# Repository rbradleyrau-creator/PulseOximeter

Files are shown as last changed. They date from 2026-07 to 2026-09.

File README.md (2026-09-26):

# Personal Pulse Oximeter

This repository contains the schematics, designs, and other information regarding the design of a personal Pulse Oximeter. As part of the design process, the overal pulse oximeter design was broken up into three smaller milestones to allow for easier testing and prototyping before moving on to a final design. More information on each of these milestones and the final design can be found via the links below.

## Milestone 1: SpO2 & HR Sensor 

  This milestone involves creating a breakout board that isolates the sensor to be used in the final system. The implementation includes an Optical Pulse Oximeter/Heart-Rate Sensor and a linear voltage regular connected to headers. Through this, an external processor can be programmed to interface with the sensor and testing can be performed to determine the best layout in the final design. This board will also be used to write firmware for the final design. 

  [Read More](https://github.com/rbradleyrau-creator/PulseOximeter/tree/main/Milestone_1%3ASpO2_%26_HR_Sensor)
  
## Milestone 2: STM32UO73KC Development Board 

  In this milestone, the pins of an STM32UO73KCU6 is connected to various headers for use in testing. In addition to the processor, the PCB also includes USB 2.0, 3.3V Buck Converter, and optional Battery power/charging. The goal of this milestone is to begin writing programs to the STM32 via USB/SWD for use in the final design and to determine the efficiency in of various batteries in powering the system.

  [Read More](https://github.com/rbradleyrau-creator/PulseOximeter/tree/main/Milestone_2%3ASTM32U073KC_Development_Board)

## Milestone 3: Display

  The main goal of this milestone is to write firmware for the STM32 that displays information to an IPS LCD Display. To begin writing this firmware, a 13P FFC breakout board was developed to allow the previously designed development board to interface with the chosen display.

  [Read More](https://github.com/rbradleyrau-creator/PulseOximeter/tree/main/Milestone_3%3ALCD_Display)

# Final Design [WIP]

  The final design for this project includes an SpO2/HR sensor connected to an STM32. The STM32 reads data from the sensor and displays it to the LCD display. The system incorporates a battery for portable use with a USB port for charging. The system also enters deep sleep when not in use which is controlled via an ON/OFF switch. The display features both the heartrate readings, SpO2 readings, and the remaining battery life. All the previously mentioned parts are combined into a single, double-sided PCB and encased inside a 3D printed enclosure. This enclosure includes padding just below the sensor along with an adjustable band allowing the device to be mounted to a finger.

  [Read More](https://github.com/rbradleyrau-creator/PulseOximeter/tree/main/Final_Design)

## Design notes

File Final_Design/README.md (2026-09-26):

# Final Design
<div align="center">
  <div style="overflow-x: auto; gap: 10px; padding-bottom: 10px; white-space: nowrap; display: inline-block; margin-right: 10px;">
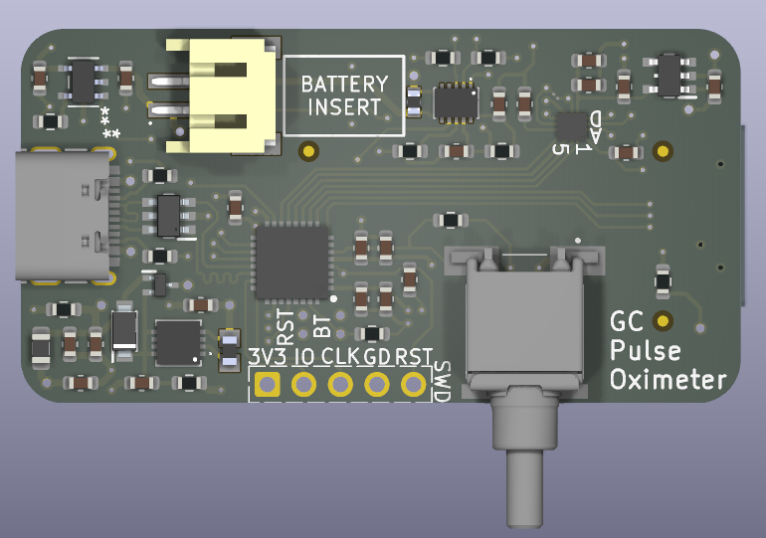
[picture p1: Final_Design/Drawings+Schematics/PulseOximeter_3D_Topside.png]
    
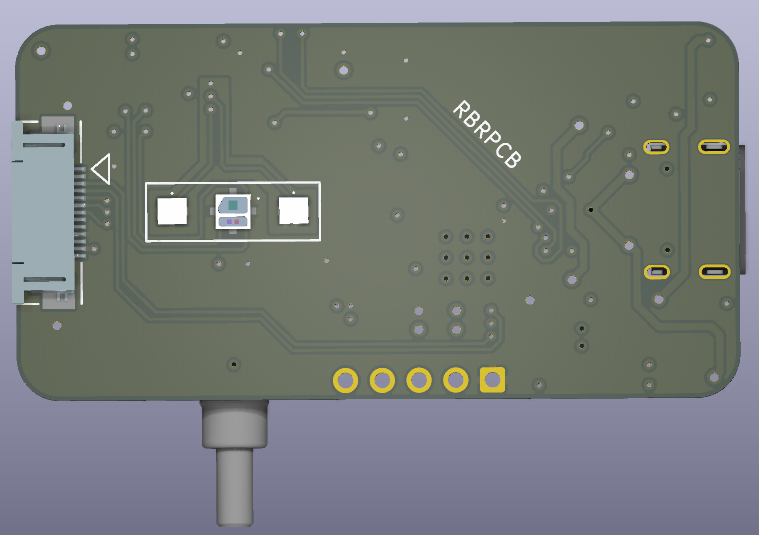
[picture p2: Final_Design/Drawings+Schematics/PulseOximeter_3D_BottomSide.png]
    
  </div>
  <br>
  
  <details>
    <summary><b>Click here to expand Copper Layers</b></summary>
    <br>
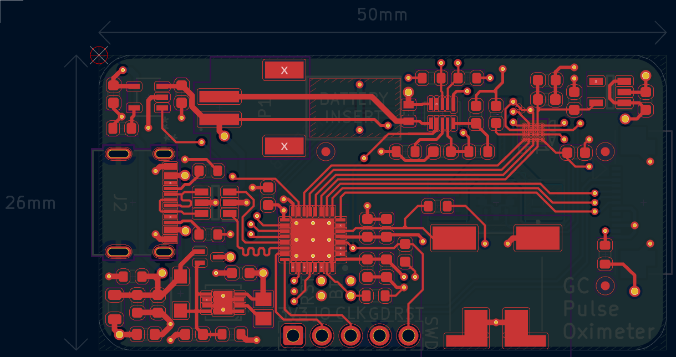
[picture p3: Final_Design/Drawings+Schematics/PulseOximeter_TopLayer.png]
    
    <hr>
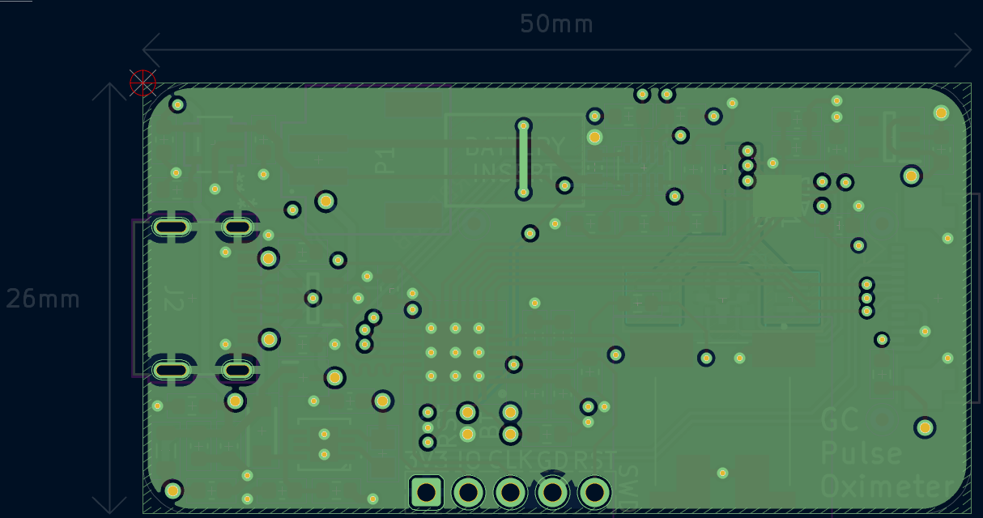
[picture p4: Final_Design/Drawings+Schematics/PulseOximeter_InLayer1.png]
SInner Layer 1
    
    <hr>
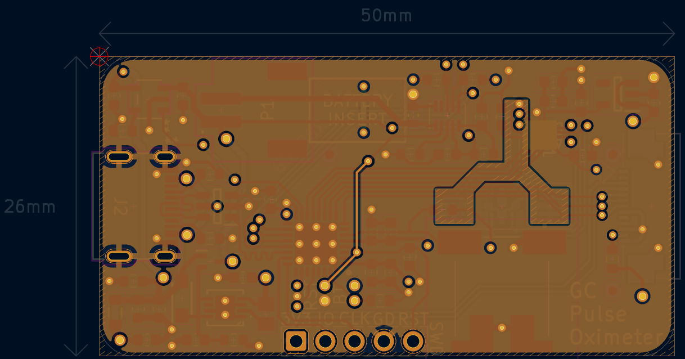
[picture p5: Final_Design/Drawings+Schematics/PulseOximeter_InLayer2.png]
Inner Layer 2
    
    <hr>
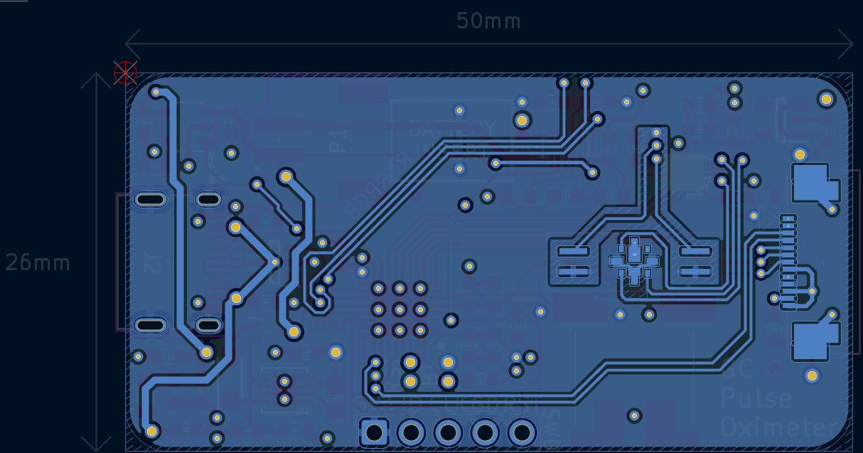
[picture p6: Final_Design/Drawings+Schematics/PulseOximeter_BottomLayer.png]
Bottom Layer
    
  </details>
</div>

<br>

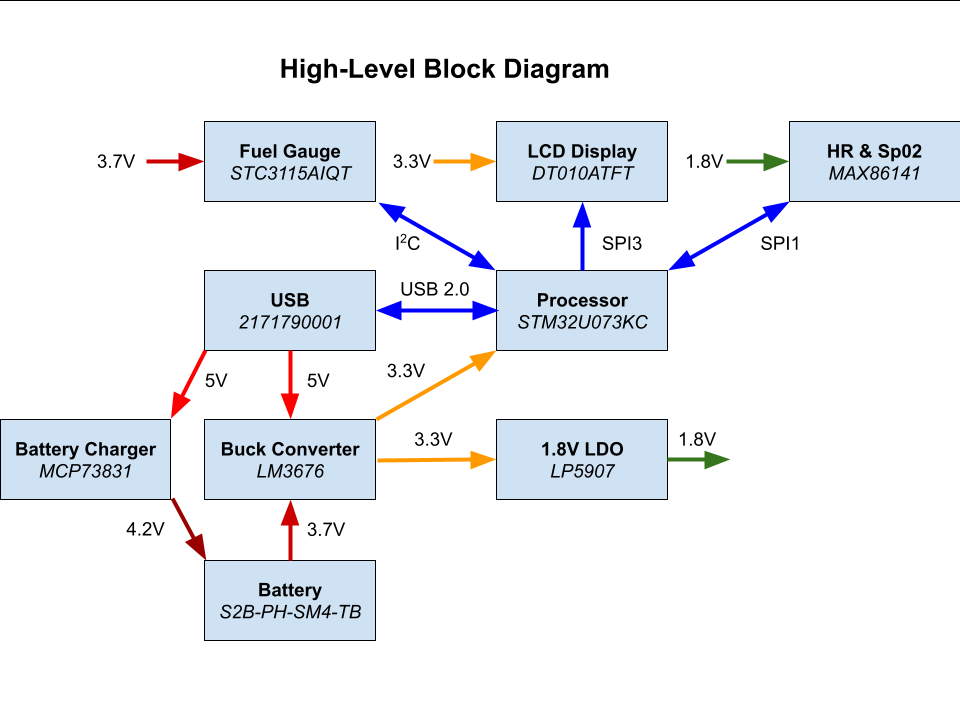
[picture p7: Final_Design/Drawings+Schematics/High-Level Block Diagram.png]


### Project Overview & Features
The final design consists of two major parts:
  - A PCBA containing each critical component
  - A 3D Modeled Enclosure to house the PCBA 

The PCB for the pulse oximeter combines all of the previous features into a singular board, with the STC3115AIQT as an exception. The board consists of an STM32U073KC processor connected to three peripherals: the STC3115AIQT fuel gauge over I2C, the MAX86141 HR/Sp02 sensor over SPI1, and an FFC connector over SPI3 for interfacing with the DT010ATFT LCD display. In addition, the processor is also connected to USB 2.0 and has SWD, boot, and reset access via exposed plated through holes. 

<br clear="right"/>
  Aside from those connections, the board operates on 3.3Vwhich is provided by the LM3676 buck converter. This component is supplied with anywhere from 5.5V (USB) to 3.0V (Battery), all of which are valid voltages for the LM3676 and a large factor for why the part was chosen. The board also includes MCP73831T battery charger which charges the battery whilst the USB is connected. 
  <br><br>
  The enclosure that houses this PCB measures at 3cm wide, 6cm long, and approximately 2cm tall and is designed for 3D printing. It is separated into two pieces that contain four dowels for a secure connection, however, the strength of this connection varies from printer to printer. In addition, the enclosure provides four openings in its casing: one at the bottom for the LED and photodiodes of the sensor, one at the top for the LCD Display, one on the side for the ON/OFF button, and one in the rear for USB port access. 

### Design Process

  The main schematic design of the PCB is largely a combination of the previous three boards into one singular board, however with some exceptions. Firstly, the TPB4056B battery charger was replaced with the MCP73831T. This was due to the fact that the TPB took up significant area on the PCB and was no longer available at the selected PCB manufacturer. A second change was the inclusion of the STC3115AIQT fuel gauge. This part was included in order to better gauge the battery life of the attached 3.7V Li-ion battery, since the discharge curve of Li-ion batteries are largely non-linear. One final design decision was the inclusion of plated through-holes for debugging. The decision was made in order to debug the newly included component and to avoid additional costs incurred due to additional manufacturing. 
  <br><br>
	For layout, the design was based around a centralized STM32 with the external connectors (USB, PH connector, ON/OFF switch, etc) being positioned in a way that made sense with the intended device enclosure. The board stack up was 4 layers with the top and bottom layers acting as signal layers and the internal layers as ground planes (with a few exceptions). One major design challenge that came up in the making of this board was the 3.3V plane that existed on the bottom of the board. Due to the large number of interconnections, this plane was broken up in several areas leading to vias being omitted from the plane or being connected by thin copper polygons. To fix this issue, components were moved to areas where they could source higher current in addition to a bridge through layer 2 to connect two un-connected polygons in the plane.
  <br><br>
	A second challenge in the design came from the placement of the LM3676 buck converter in relation to the USB data lines. Due to the required placement of the PH connector, the buck converter was located in the bottom left corner. To prevent the high-frequency switching from affecting sensitive components,  sensitive ICs like the MAX86141 IC were placed in the opposite corner of the board. However, the data lines of the USB could not be relocated. To minimize the effect this switching would have on these lines, the STM32 was shifted upward to allow the maximum distance between the data lines and the offending trace. This distance ended up being 5 times larger than the trace width of the data lines, providing satisfactory protection for full-speed USB.
  <br><br>
	A third challenge that came up in the design was the routing of SPI. Originally, the board was designed to operate with only one MOSI & MISO. However, this would have required a star connection scheme, resulting in disconnected ends causing reflections and ringing. To remove this factor, tertiary SPI pins on the STM32 were used to set up two separate communications. While this did take up more real estate on the board, it did allow for the display and MAX86141 connections to operate at different clocking frequencies which allowed the refresh rate of the DT010ATFT to quadruple. 

### Testing and Results

 As of 9/26/2026, the board is still in manufacturing and will be programmed and validated upon arrival. 

## List of Major Components/Datasheets

Sensors/Processors <br>
 - [STM32U073KCU6](https://www.st.com/resource/en/datasheet/stm32u073c8.pdf) <br>
 - [HR/Sp02 Sensor - MAX86141](https://www.analog.com/media/en/technical-documentation/data-sheets/max86140-max86141.pdf) <br>
 - [Fuel Gauge -STC3115AIQT](https://www.st.com/content/ccc/resource/technical/document/datasheet/24/05/c6/c7/0c/72/41/39/DM00066800.pdf/files/DM00066800.pdf/jcr:content/translations/en.DM00066800.pdf) <br>

Power 
- [Buck Converter - LM3676](https://www.ti.com/lit/ds/symlink/lm3676.pdf?ts=1784331233319&ref_url=https%253A%252F%252Fwww.ti.com%252Fproduct%252FLM3676) <br>
- [Battery Charger IC - MCP73831](https://www.mouser.com/datasheet/3/282/1/MCP73831_Family_Data_Sheet_DS20001984H.pdf) <br>
- [LDO - LP5907](https://www.ti.com/lit/ds/symlink/lp5907.pdf) <br>

Diodes/MOSFETs
- [Schottky Diode - NSR0620P2](https://www.onsemi.com/pdf/datasheet/nsr0620p2-d.pdf) <br>
- [P-Channel MOSFET - DMG1013T](https://www.diodes.com/datasheet/download/DMG1013T.pdf) <br>
- [ESD Diodes - USBLC6-2SC6Y](https://www.st.com/resource/en/datasheet/usblc6-2sc6y.pdf) <br>
- [LED(s) - SFH 7018B](https://www.mouser.com/datasheet/3/5912/1/SFH_7018B_EN.pdf) <br>
- [Photodiode - SFH 2704](https://www.mouser.com/datasheet/3/5912/1/SFH_2704_EN.pdf) <br>

Connectors
- [USB Connector - 2171790001](https://www.molex.com/en-us/products/part-detail/2171790001?display=pdf&utm_source=M2X&utm_medium=api&utm_campaign=api&utm_id=M2X_API?utm_source=M2X&utm_medium=api&utm_campaign=api&utm_id=M2X_API) <br>
- [13P FFC Connector - 527451397](https://www.molex.com/en-us/products/part-detail-pdf/527451397?display=pdf) <br>
- [Battery Connector - S2B-PH-SM4-TB](https://www.jst-mfg.com/product/pdf/eng/ePH.pdf) <br>
- [ON/OFF Switch - EP11SD1SAPE](https://www.littelfuse.com/assetdocs/littelfuse-ck-pushbutton-ep-series-datasheet?assetguid=1bab3baa-d70e-403b-9074-f0060fd8bd56)<br>

Peripherals
- [LCD Display - DT010ATFT](https://www.mouser.com/datasheet/3/3687/1/DT010ATFT-Rev1_1-Displaytech-Spec.pdf) <br>
- [Battery - 3.7V Li-ion](https://cdn-shop.adafruit.com/product-files/1570/1570datasheet.pdf) <br>

***

### [Return to Project Page](https://github.com/rbradleyrau-creator/PulseOximeter/tree/main) <br>

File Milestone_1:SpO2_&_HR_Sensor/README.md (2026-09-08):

# MAX86141 Breakout Board
<div align="center">
  <div style="overflow-x: auto; gap: 10px; padding-bottom: 10px; white-space: nowrap; display: inline-block; margin-right: 10px;">
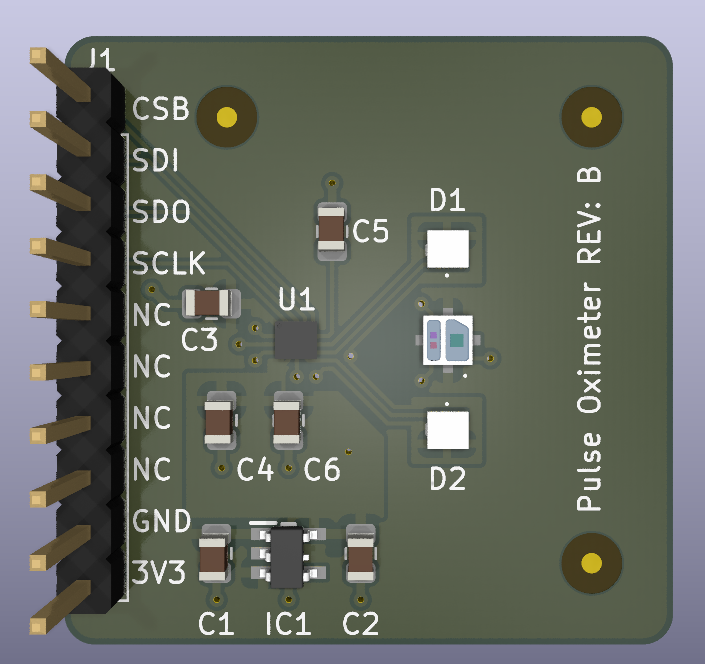
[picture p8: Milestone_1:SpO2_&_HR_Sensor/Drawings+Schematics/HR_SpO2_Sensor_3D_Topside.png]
    
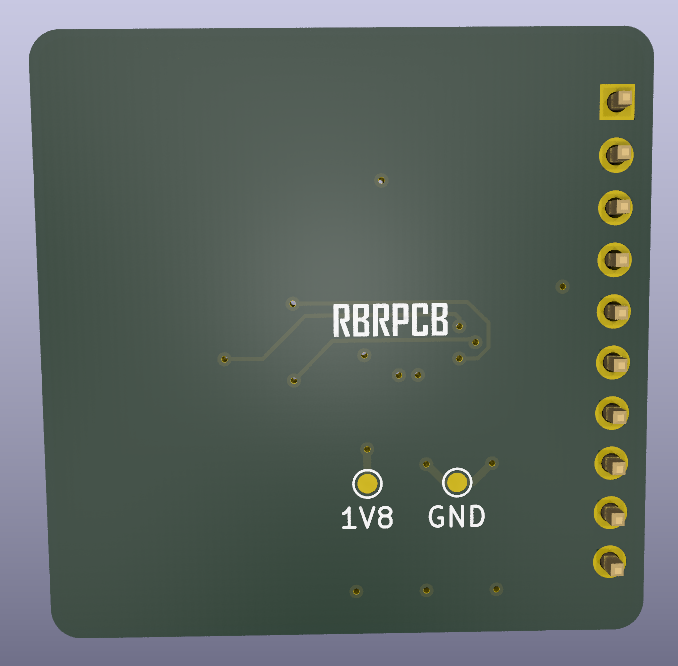
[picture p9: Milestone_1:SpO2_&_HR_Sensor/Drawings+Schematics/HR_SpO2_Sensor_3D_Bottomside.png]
    
  </div>
  <br>
  
  <details>
    <summary><b>Click here to expand Copper Layers</b></summary>
    <br>
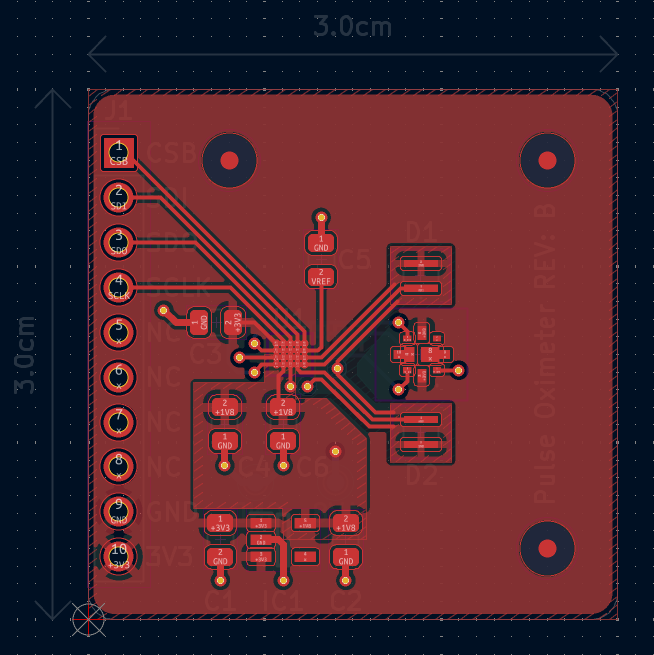
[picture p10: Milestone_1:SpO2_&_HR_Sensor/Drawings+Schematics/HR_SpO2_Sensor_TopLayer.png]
    
    <hr>
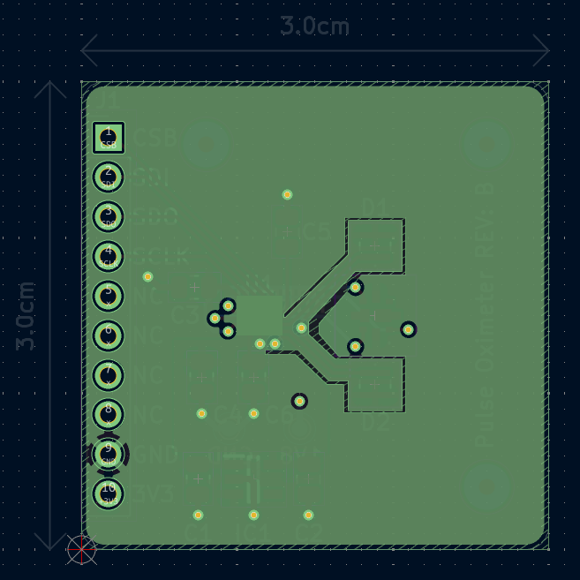
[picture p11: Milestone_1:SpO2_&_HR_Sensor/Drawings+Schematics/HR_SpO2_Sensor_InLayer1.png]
Inner Layer 1
    
    <hr>
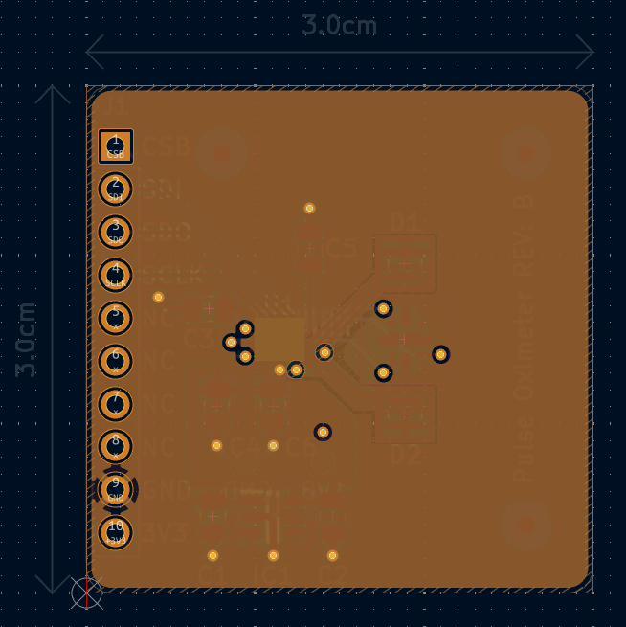
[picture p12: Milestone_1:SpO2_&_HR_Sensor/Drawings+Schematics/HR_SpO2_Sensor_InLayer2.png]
Inner Layer 2
    
    <hr>
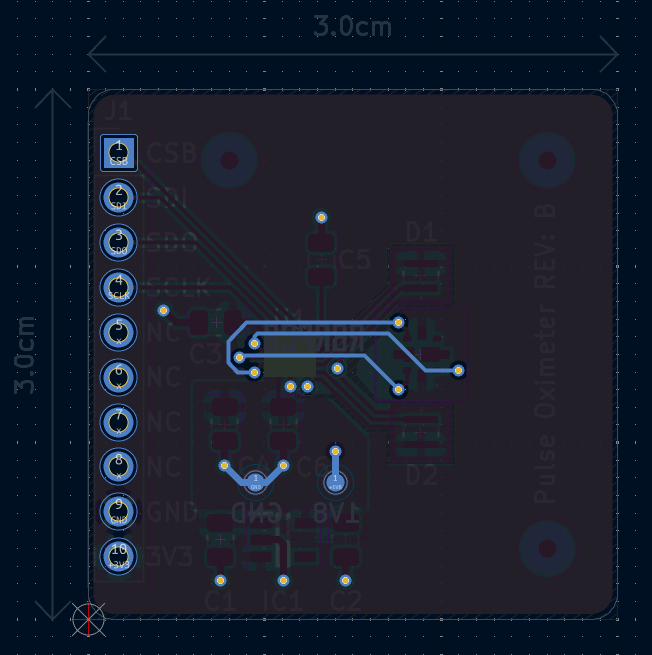
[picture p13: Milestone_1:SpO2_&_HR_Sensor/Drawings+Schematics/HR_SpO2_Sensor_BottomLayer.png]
Bottom Layer
    
  </details>
</div>

  In order to test and write firmware for the MAX86141 HR/SpO2 sensor, a breakout board was created. The board includes the MAX86141 itself, along with 1 LED emitter emitting infrared, 
  red, and green light, and 2 photodiodes for interpreting the reflections of these light waves. In addition to that, a 1.8V linear regulator is included to power the sensor. 
<br> <br>
  The board can be interfaced with via the pin headers on the left-hand side. The 3.3V pin provides power to the aforementioned LDO, LED, and LED drivers (in the MAX86141) and 
  the Ground pin provided a common ground between the internal and external systems. The top 4 pins (CSB, SDI, SDO, SCLK) provide access to the sensor's readings via SPI.
<br> <br>
  In the prototyping phase, these pins were connected to the STM32 breakout board developed in Milestone 2 in order to develop firmware that could utilize the MAX86141. After testing 
  several different MAX configurations, the best configuration for the final design's low power application was found to be 128 samples per second with an averaging of 2 (so 64 data samples
  per second). For Sp02, the led driver current to the red and IR led were adjusted until their ratio provided accurate readings. For HR, the sensor data was tested with multiple algorithms
  before settling on an implementation developed by Raquel Gutiérrez-Rivas and colleagues. This algorithm was then applied to samples of data for the prototype tests and was adjusted until it 
  met a reasonable level of accuracy. 

## List of Major Components/Datasheets

- [MAX86141](https://www.analog.com/media/en/technical-documentation/data-sheets/max86140-max86141.pdf) <br>
- [LDO - LP5907](https://www.ti.com/lit/ds/symlink/lp5907.pdf) <br>
- [LED(s) - SFH 7018B](https://www.mouser.com/datasheet/3/5912/1/SFH_7018B_EN.pdf) <br>
- [Photodiode - SFH 2704](https://www.mouser.com/datasheet/3/5912/1/SFH_2704_EN.pdf) <br>

## List of External Resources

- [HR Algorithm Paper](https://ieeexplore.ieee.org/abstract/document/7138573) <br>
- [Desmos HR Data Analysis](https://www.desmos.com/calculator/z13ruce9kt) <br>

***

### [Return to Project Page](https://github.com/rbradleyrau-creator/PulseOximeter/tree/main) <br>

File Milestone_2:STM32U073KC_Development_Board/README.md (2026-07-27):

# STM32U073KC Development Board
<div align="center">
  <div style="overflow-x: auto; gap: 10px; padding-bottom: 10px; white-space: nowrap; display: inline-block; margin-right: 10px;">
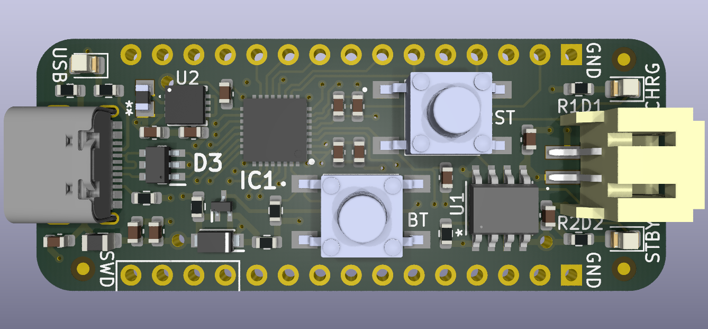
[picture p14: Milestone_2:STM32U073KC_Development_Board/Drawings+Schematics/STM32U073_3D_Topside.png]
    
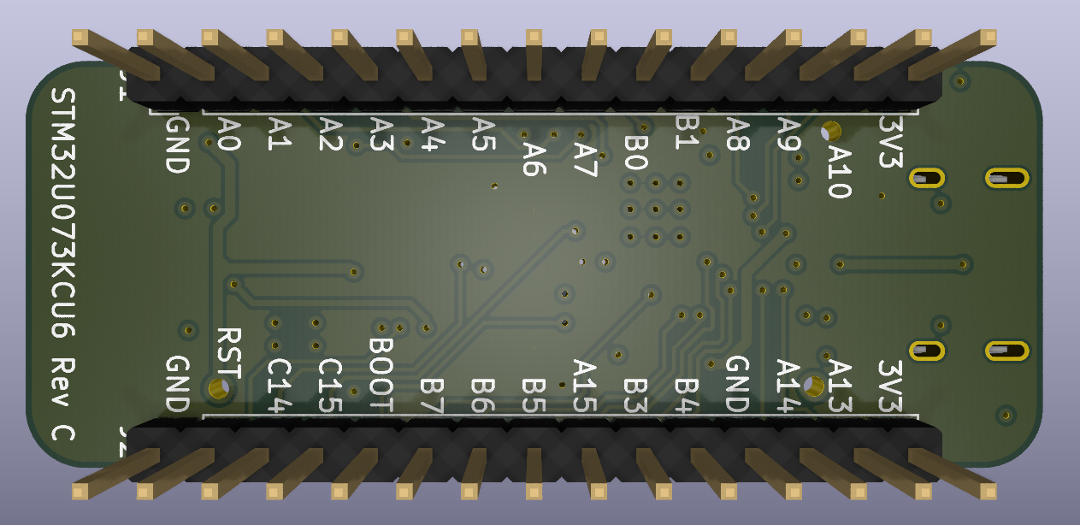
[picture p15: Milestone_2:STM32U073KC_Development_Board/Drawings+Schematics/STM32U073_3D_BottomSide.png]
    
  </div>
  <br>
  
  <details>
    <summary><b>Click here to expand Copper Layers</b></summary>
    <br>
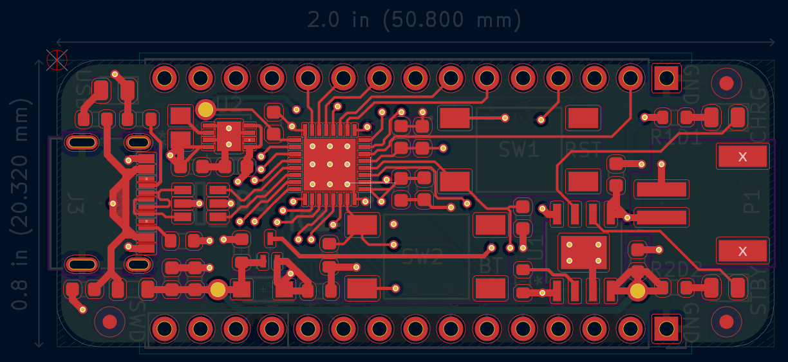
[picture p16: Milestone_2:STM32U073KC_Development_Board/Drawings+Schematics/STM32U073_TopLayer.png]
    
    <hr>
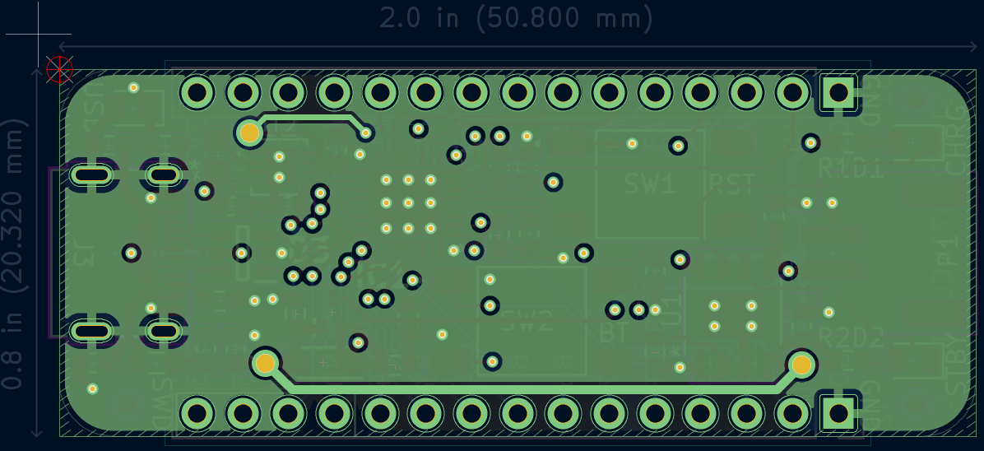
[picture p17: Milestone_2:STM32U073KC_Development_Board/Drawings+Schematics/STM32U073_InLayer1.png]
SInner Layer 1
    
    <hr>
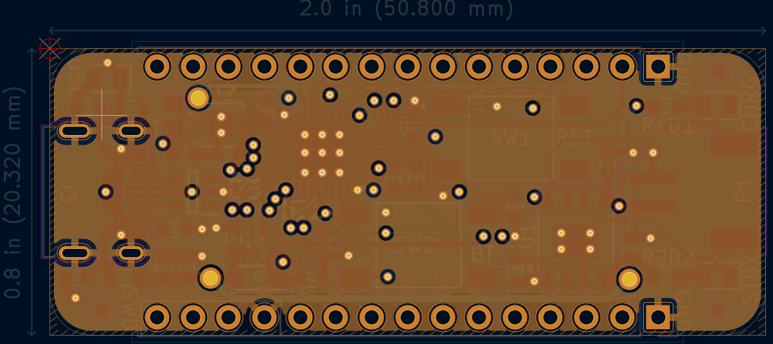
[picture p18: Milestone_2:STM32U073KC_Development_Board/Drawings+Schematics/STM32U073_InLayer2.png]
Inner Layer 2
    
    <hr>
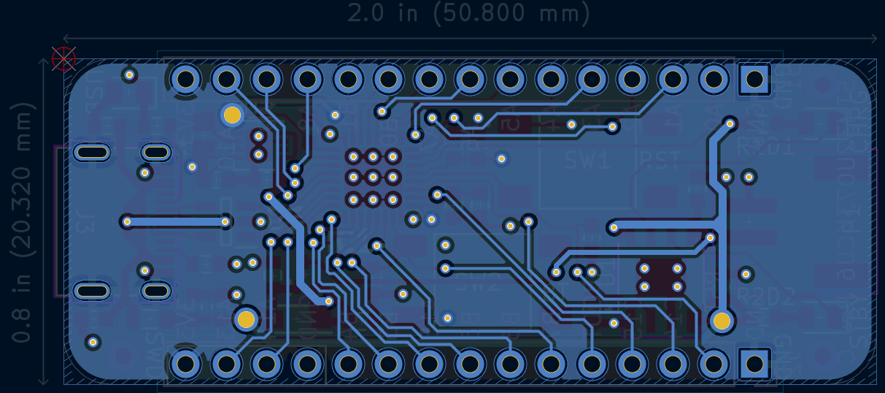
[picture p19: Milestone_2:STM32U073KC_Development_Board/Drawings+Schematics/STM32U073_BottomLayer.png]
Bottom Layer
    
  </details>
</div>

  This PCB Design utilizes an STM32U073KCU6 as its central processor. The board involes a USB header which enables Full Speed USB 2.0 communication with ESD protection and filtered 5 volts of potential throughout the board. This voltage is connected to an LM3676 buck converter that steps the voltage down to 3.3V. Additionally, the 5V provided by a USB connection is connected to a TPB4056B Battery Charging IC to charge a connected battery. Power for the board can also (optionally) be provided via a battery. For this design, a 3.7V Li-Polymer battery is recommended. A connected battery can continue to provide power to the system up until the voltage accross its terminals reaches a minimum of 3.0V. However, while the STM32 will continue to operate at this voltage, care should be taken to ensure that connected peripherals can also operate at this voltage. 
<br> <br>
  Power to the system will be provided via USB if one is connected, otherwise it will be provided via the connected battery. This feature is achieved by using a Schottky diode in addition to a P-channel MOSFET. Once the USB is connected, the 5V provided to the MOSFET's Gate will prevent current flow from the source to the drain, essentially disconnecting the battery from the buck converter. When the USB is disconnected, backflow to the 5V line (which is now grounded) is prevented via the previously mentioned diode.
<br> <br>
  Other features include: Boot and Reset buttons and LED indicators for charging, charge standby, and USB connection. 

## List of Major Components/Datasheets

- [STM32U073KCU6](https://www.st.com/resource/en/datasheet/stm32u073c8.pdf) <br>
- [Buck Converter - LM3676](https://www.ti.com/lit/ds/symlink/lm3676.pdf?ts=1784331233319&ref_url=https%253A%252F%252Fwww.ti.com%252Fproduct%252FLM3676) <br>
- [Battery Charger IC - TPB4056B](https://static.3peak.com/res/doc/ds/Datasheet_TPB4056B.pdf) <br>
- [Schottky Diode - NSR0620P2](https://www.onsemi.com/pdf/datasheet/nsr0620p2-d.pdf) <br>
- [P-Channel MOSFET - DMG1013T](https://www.diodes.com/datasheet/download/DMG1013T.pdf) <br>
- [ESD Diodes - USBLC6-2SC6Y](https://www.st.com/resource/en/datasheet/usblc6-2sc6y.pdf) <br>
- [USB Connector - 2171790001](https://www.molex.com/en-us/products/part-detail/2171790001?display=pdf&utm_source=M2X&utm_medium=api&utm_campaign=api&utm_id=M2X_API?utm_source=M2X&utm_medium=api&utm_campaign=api&utm_id=M2X_API) <br>
- [Battery Connector - S2B-PH-SM4-TB](https://www.jst-mfg.com/product/pdf/eng/ePH.pdf) <br>

***

### [Return to Project Page](https://github.com/rbradleyrau-creator/PulseOximeter/tree/main) <br>

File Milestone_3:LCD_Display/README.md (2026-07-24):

# (DT010ATFT) LCD Display

  The final design will feature heartrate, SpO2, and battery life readings on an LCD Display. The goal of this milestone is to: A) create a breakout board that allows the chosen display to interface with the microcontroller developed in the previous milestone, and B) develop firmware for displaying the output of various sensors. To begin this process, a breakout board was made that converts a 13 position FFC (flexible flat cable) into a breakout of 13 pins, plus one extra for shield connection. This board can be seen below.
<br> <br>
  The final step of this process required that LCD libraries be installed and utilized to display the intended data. To do this, research had to be conducted to find suitable libraries and learn their implementations. Once this information was finalized, the library would be implemented into a firmware program that will be used in the final design. 
<br> <br>
  As of July 23rd, 2026, this milestone is still a work in progress.

## 13P FFC Breakout Board

<div align="center">
  <div style="overflow-x: auto; gap: 10px; padding-bottom: 10px; white-space: nowrap; display: inline-block; margin-right: 10px;">
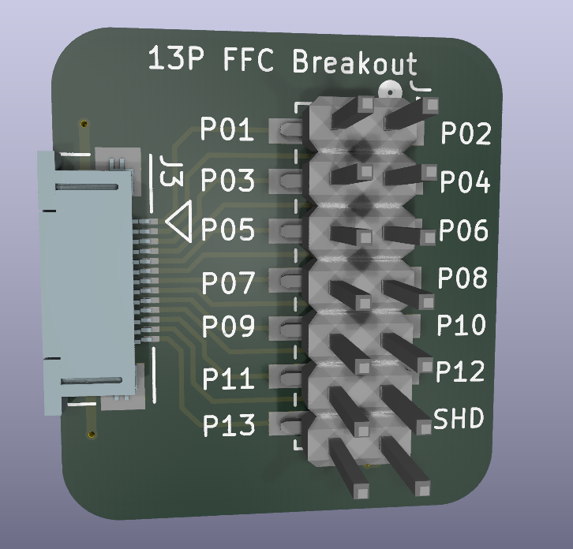
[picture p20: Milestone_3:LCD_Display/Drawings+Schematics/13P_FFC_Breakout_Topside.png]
    
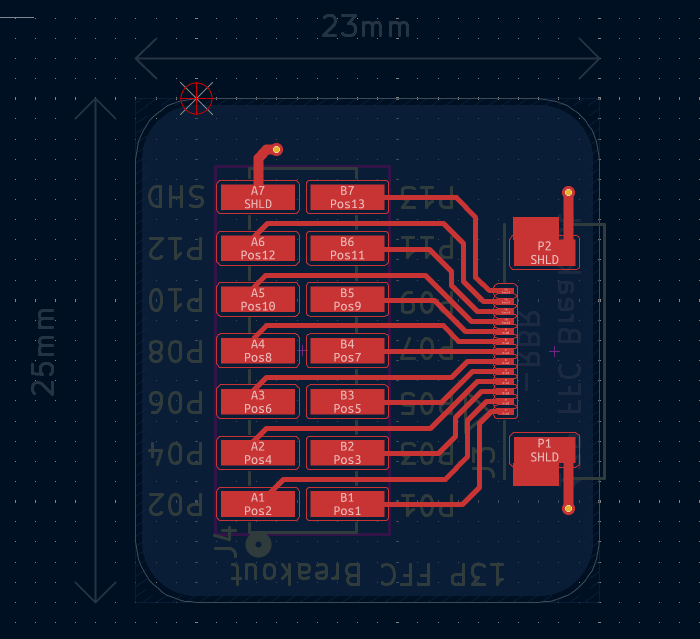
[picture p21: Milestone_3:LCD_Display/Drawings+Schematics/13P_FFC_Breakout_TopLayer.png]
    
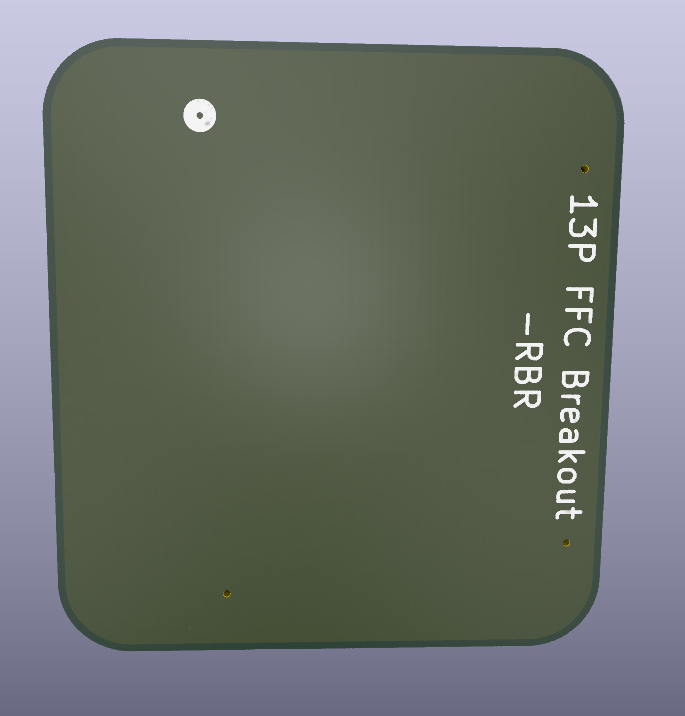
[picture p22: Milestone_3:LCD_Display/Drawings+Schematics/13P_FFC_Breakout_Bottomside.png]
    
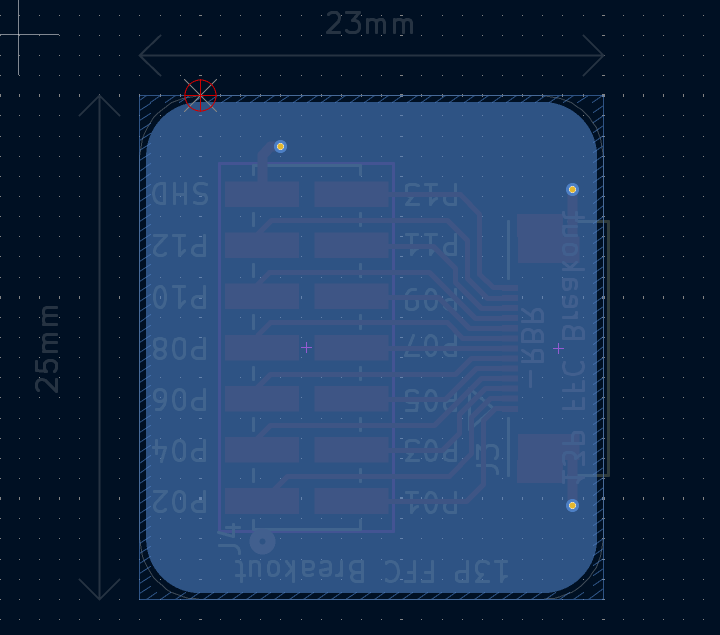
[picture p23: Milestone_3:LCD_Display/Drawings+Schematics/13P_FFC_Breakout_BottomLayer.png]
    
  </div>
</div>

## List of Major Components/Datasheets

- [LCD Display - DT010ATFT](https://www.mouser.com/datasheet/3/3687/1/DT010ATFT-Rev1_1-Displaytech-Spec.pdf) <br>
- [2x7 Surface Mounted Pins - 15910140](https://www.molex.com/en-us/products/part-detail-pdf/15910140?display=pdf) <br>
- [13P FFC Connector - 527451397](https://www.molex.com/en-us/products/part-detail-pdf/527451397?display=pdf) <br>

***

### [Return to Project Page](https://github.com/rbradleyrau-creator/PulseOximeter/tree/main) <br>

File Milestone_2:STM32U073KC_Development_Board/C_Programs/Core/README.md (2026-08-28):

## Important Note:

graphics.c & graphics.h depend on 3 files: 'ST7735.h', 'GFX_FUNCTION.h', & 'fonts.h'. These files are protected by a license prohibiting redistribution and can only be accessed/downloaded via their webpage link below.

https://controllerstech.com/st7735-1-8-tft-display-with-stm32/#goog_rewarded

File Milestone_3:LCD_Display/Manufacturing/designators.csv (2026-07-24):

J3:1
J4:1

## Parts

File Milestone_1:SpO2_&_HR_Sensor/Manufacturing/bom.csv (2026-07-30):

Designator | Footprint | Quantity | Value | LCSC Part #
C1, C2, C5 | 0805 | 3 | 1µF
C3 | 0805 | 1 | 10µF
C4 | 0805 | 1 | 22µF
C6 | 0805 | 1 | 0.1µF
D1, D2 | SFH2704 | 2 | SFH_2704
IC1 | SOT95P280X145-5N | 1 | LP5907MFX-1.8_NOPB
J1 | PinHeader_1x10_P2.54mm_Vertical | 1 | Conn_01x10
LED1 | SFH7018B | 1 | SFH_7018B
TP3 | TestPoint_Pad_D1.0mm | 1 | 1V8
TP4 | TestPoint_Pad_D1.0mm | 1 | GND
U1 | 21-100134A_20_MXM | 1 | MAX86141ENP+

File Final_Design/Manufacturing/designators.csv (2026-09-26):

C1:1
C10:1
C11:1
C12:1
C13:1
C14:1
C15:1
C16:1
C17:1
C18:1
C19:1
C2:1
C20:1
C21:1
C3:1
C4:1
C5:1
C6:1
C7:1
C8:1
C9:1
D1:1
D2:1
D3:1
D4:1
FB1:1
IC1:1
IC2:1
J1:1
J2:1
J3:1
L1:1
LED1:1
NT1:1
P1:1
Q1:1
R1:1
R10:1
R11:1
R14:1
R2:1
R3:1
R5:1
R6:1
R7:1
R8:1
R9:1
REF**:3
R_FILT1:1
R_PROG1:1
S1:1
U1:1
U2:1
U3:1
U4:1

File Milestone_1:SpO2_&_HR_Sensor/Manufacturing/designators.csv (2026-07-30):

C1:1
C2:1
C3:1
C4:1
C5:1
C6:1
D1:1
D2:1
IC1:1
J1:1
LED1:1
REF**:3
TP3:1
TP4:1
U1:1

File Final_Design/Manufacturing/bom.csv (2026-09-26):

Designator | Footprint | Quantity | Value | LCSC Part #
C1, C20, C4, C7 | 0603 | 4 | 100 nF
C10, C2 | 0603 | 2 | 10 µF
C11, C15 | 0603 | 2 | 220nF
C12 | 0603 | 1 | 2.2 µF
C13, C14 | 0603 | 2 | 4.7 µF
C16 | 0603 | 1 | 10 nF
C17, C21, C5 | 0603 | 3 | 1 µF
C18, C19, C8 | 0603 | 3 | 1µF
C3 | 0603 | 1 | 10µF
C6 | 0603 | 1 | 22µF
C9 | 0603 | 1 | 100nF
D1, D2 | SFH2704 | 2 | SFH_2704
D3 | SODFL3616X98N | 1 | MBR120ESFT1G
D4 | SOT95P280X145-6N | 1 | USBLC6-2SC6Y
FB1 | 0805 | 1 | 1kΩ @ 100MHz
IC1 | QFN50P500X500X60-33N-D | 1 | STM32U073KCU6
IC2 | SOT95P280X145-5N | 1 | LP5907MFX-1.8_NOPB
J1 | CON_527451397_MOL | 1 | 527451397
J2 | 2171790001_MOL | 1 | 2171790001
L1 | INDC2012X100N | 1 | DFE201210U-2R2M=P2
LED1 | SFH7018B | 1 | SFH_7018B
P1 | JST_S2B-PH-SM4-TB | 1 | S2B-PH-SM4-TB
Q1 | SOT50P160X90-3N | 1 | DMG1013T-7
R1 | 0603 | 1 | 100
R10, R2, R3, R9 | 0603 | 4 | 5k1
R11, R14, R5, R6 | 0603 | 4 | 100k
R7 | RES_ERJ3BWFR100V | 1 | ERJ3BWFR100V
R8, R_FILT1 | 0603 | 2 | 1k
R_PROG1 | 0603 | 1 | 20k
S1 | EP11SD1SAPE | 1 | EP11SD1SAPE
U1 | 21-100134A_20_MXM | 1 | MAX86141ENP+
U2 | DFN50P300X300X80-9N | 1 | LM3676SD-3.3 | LM3676SD-3.3
U3 | SON50P200X300X60-10 | 1 | STC3115AIQT
U4 | SOT-23-5_MC_MCH-L | 1 | MCP73831T-2ACI/OT

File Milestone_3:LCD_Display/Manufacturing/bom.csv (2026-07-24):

Designator | Footprint | Quantity | Value | LCSC Part #
J3 | CON_527451397_MOL | 1 | 527451397
J4 | CONN_713080000-SD_14_M6p10_MOL | 1 | 15910140

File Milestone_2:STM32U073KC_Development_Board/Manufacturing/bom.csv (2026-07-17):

Designator | Footprint | Quantity | Value | LCSC Part #
C1, C10, C2, C6 | 0603 | 4 | 1µF
C11, C3, C5, C7, C8 | 0603 | 5 | 100nF
C12 | 0603 | 1 | 4.7µF
C13, C4 | 0603 | 2 | 10µF
C9 | 0603 | 1 | 10nF
D1 | 0805 | 1 | ORG_LED
D2 | 0805 | 1 | BLU_LED
D3 | SOT95P280X145-6N | 1 | USBLC6-2SC6Y
D4 | 0805 | 1 | RED_LED
D5 | SODFL3616X98N | 1 | MBR120ESFT1G
FB1 | 0805 | 1 | 1kΩ @ 100MHz
IC1 | QFN50P500X500X60-33N-D | 1 | STM32U073KCU6
J3 | 2171790001_MOL | 1 | 2171790001
L1 | INDC2012X100N | 1 | DFE201210U-2R2M=P2
P1 | JST_S2B-PH-SM4-TB | 1 | S2B-PH-SM4-TB
Q1 | SOT50P160X90-3N | 1 | DMG1013T-7
R1, R6 | 0603 | 2 | 1k5
R2 | 0603 | 1 | 1k
R4, R5 | 0603 | 2 | 5k1
R7, R8, R9 | 0603 | 3 | 100k
R_P | 0603 | 1 | 24k
SW1 | SW_TS04-66-55-BK-260-SMT | 1 | RST
SW2 | SW_TS04-66-55-BK-260-SMT | 1 | BOOT
U2 | DFN50P300X300X80-9N | 1 | LM3676SD-3.3 | LM3676SD-3.3

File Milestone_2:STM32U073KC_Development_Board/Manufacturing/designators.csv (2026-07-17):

C1:1
C10:1
C11:1
C12:1
C13:1
C2:1
C3:1
C4:1
C5:1
C6:1
C7:1
C8:1
C9:1
D1:1
D2:1
D3:1
D4:1
D5:1
FB1:1
IC1:1
J1:1
J2:1
J3:1
L1:1
P1:1
Q1:1
R1:1
R2:1
R4:1
R5:1
R6:1
R7:1
R8:1
R9:1
REF**:3
R_P:1
SW1:1
SW2:1
U1:1
U2:1

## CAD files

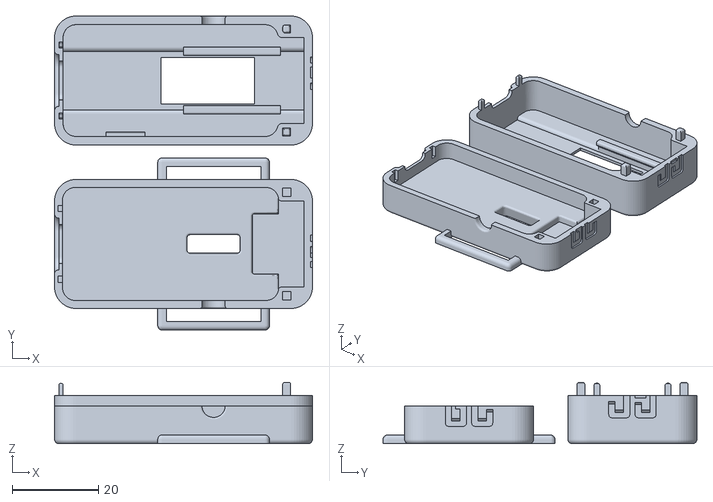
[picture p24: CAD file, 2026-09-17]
Final_Design/Pulse-Oximeter-Case.stl
60.0 x 73.0 x 14.2

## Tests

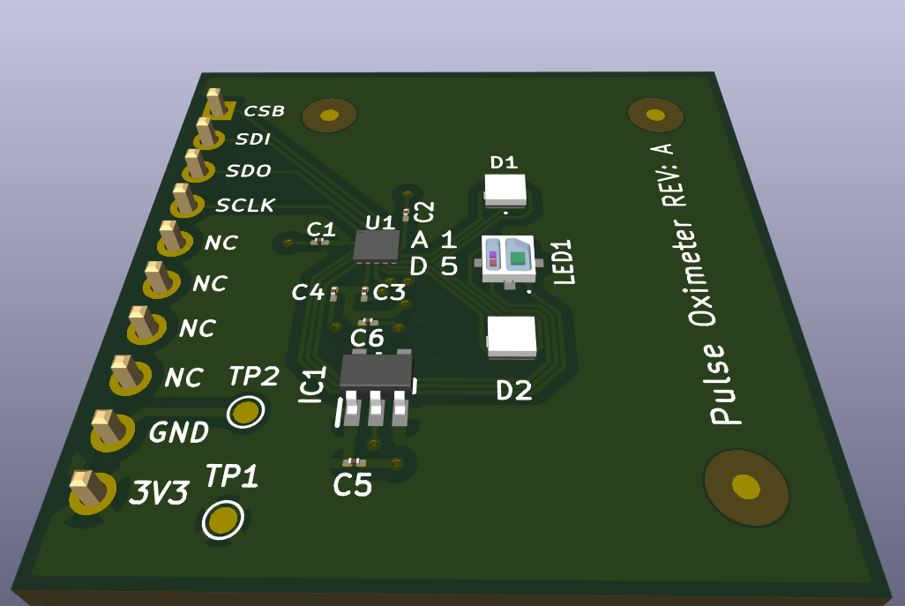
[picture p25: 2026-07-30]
Milestone_1:SpO2_&_HR_Sensor/Drawings+Schematics/PulseOxiTest_RevA_3D.png

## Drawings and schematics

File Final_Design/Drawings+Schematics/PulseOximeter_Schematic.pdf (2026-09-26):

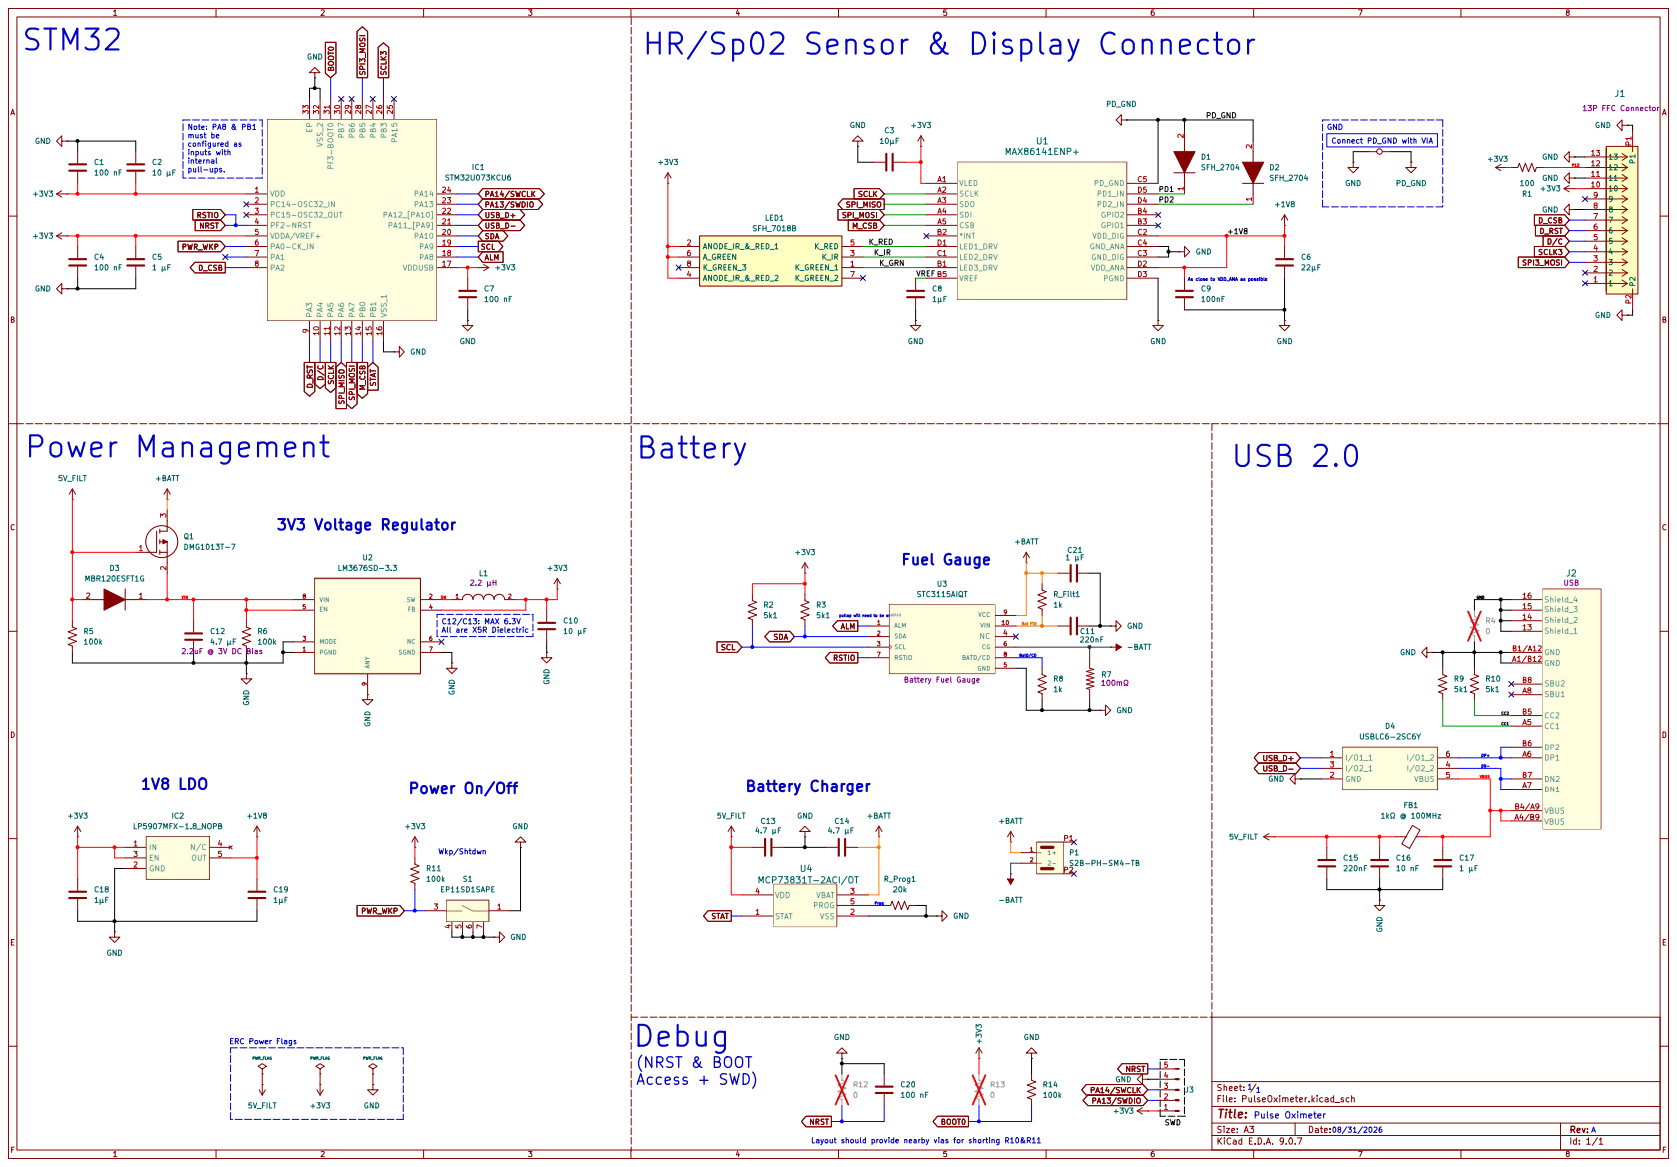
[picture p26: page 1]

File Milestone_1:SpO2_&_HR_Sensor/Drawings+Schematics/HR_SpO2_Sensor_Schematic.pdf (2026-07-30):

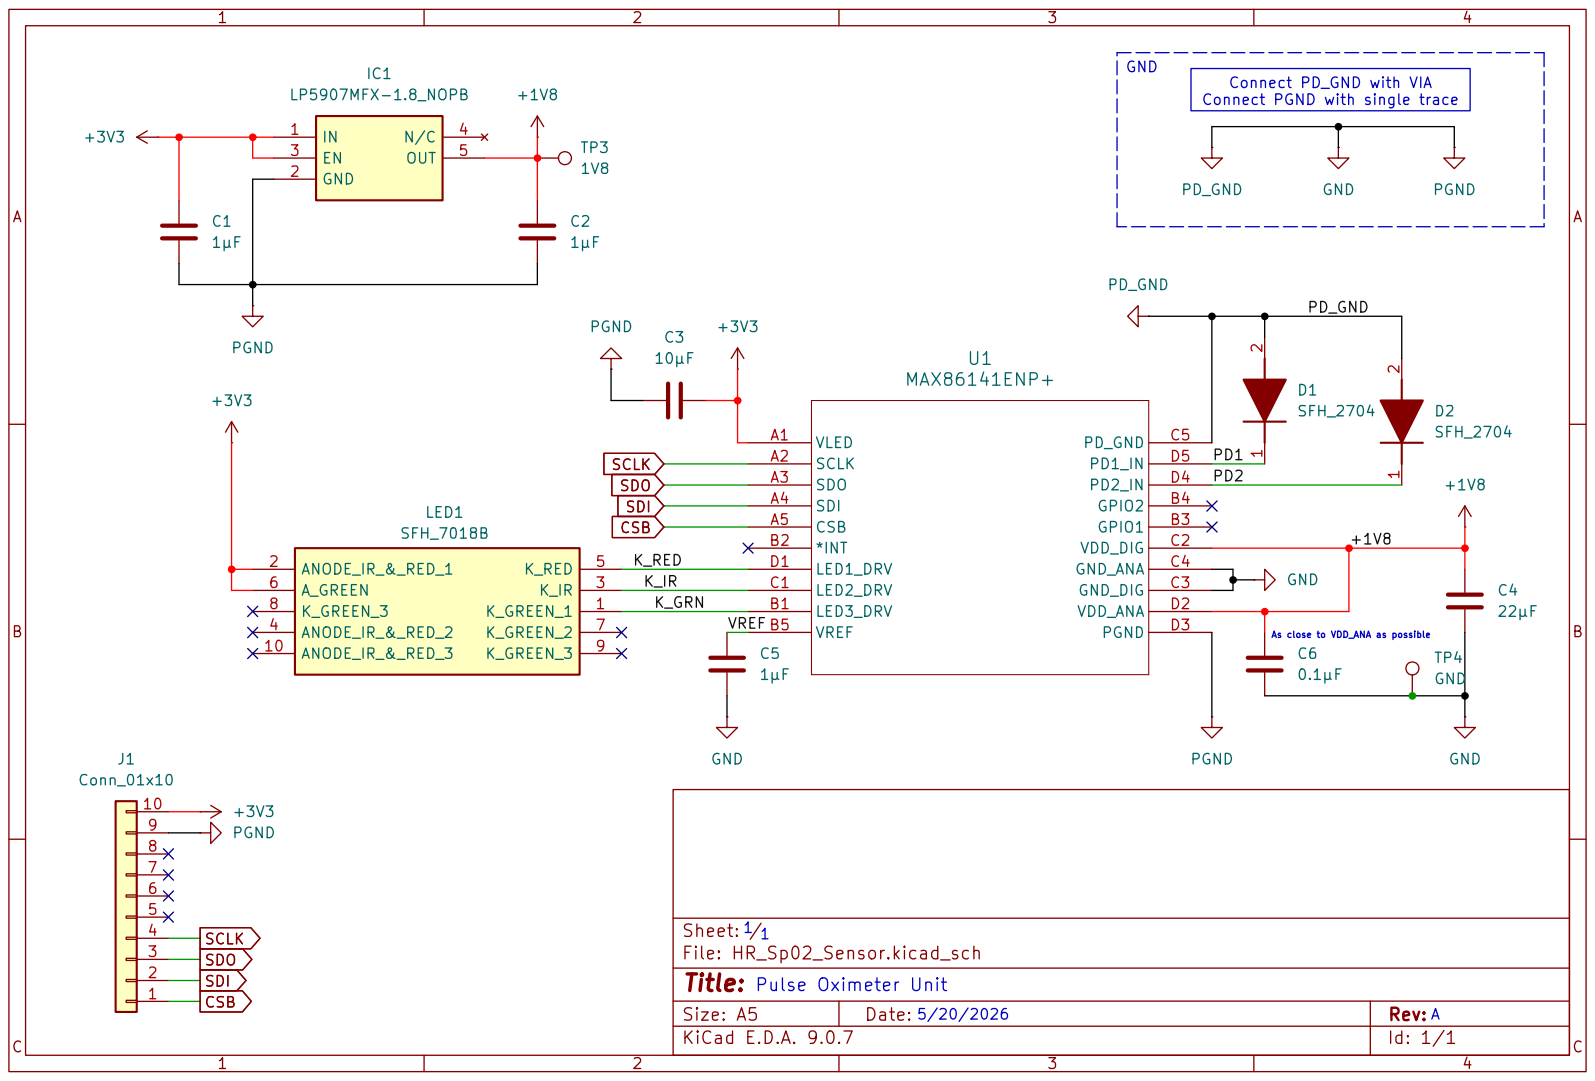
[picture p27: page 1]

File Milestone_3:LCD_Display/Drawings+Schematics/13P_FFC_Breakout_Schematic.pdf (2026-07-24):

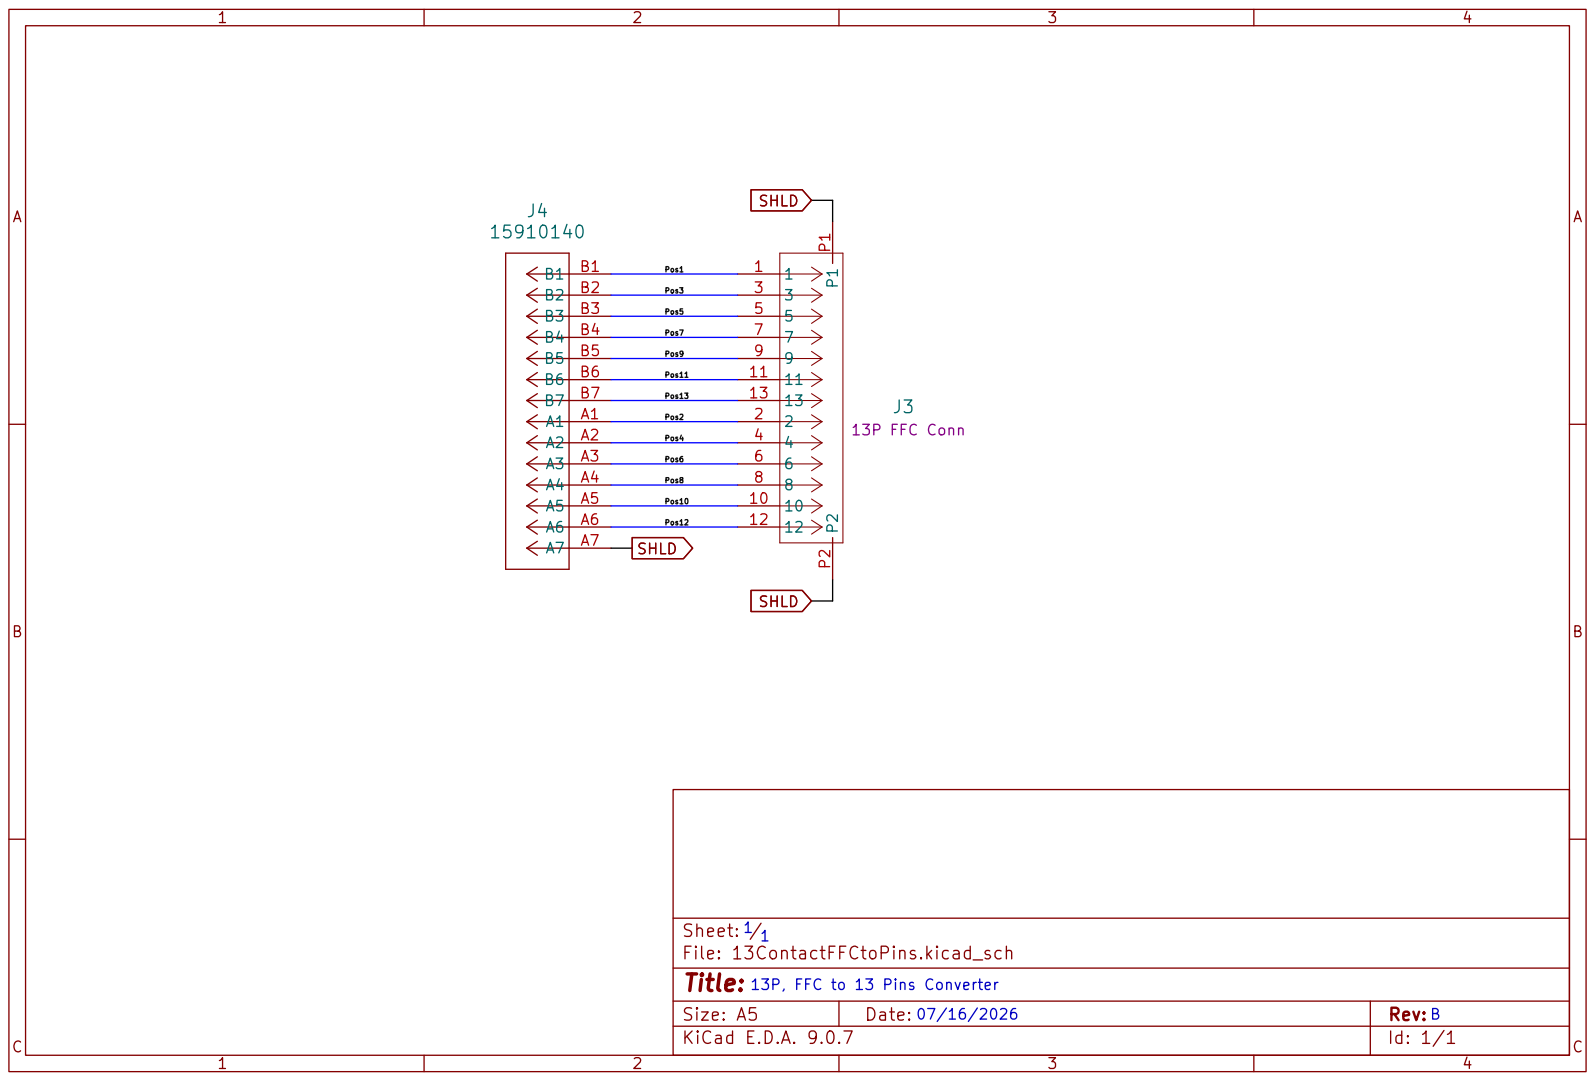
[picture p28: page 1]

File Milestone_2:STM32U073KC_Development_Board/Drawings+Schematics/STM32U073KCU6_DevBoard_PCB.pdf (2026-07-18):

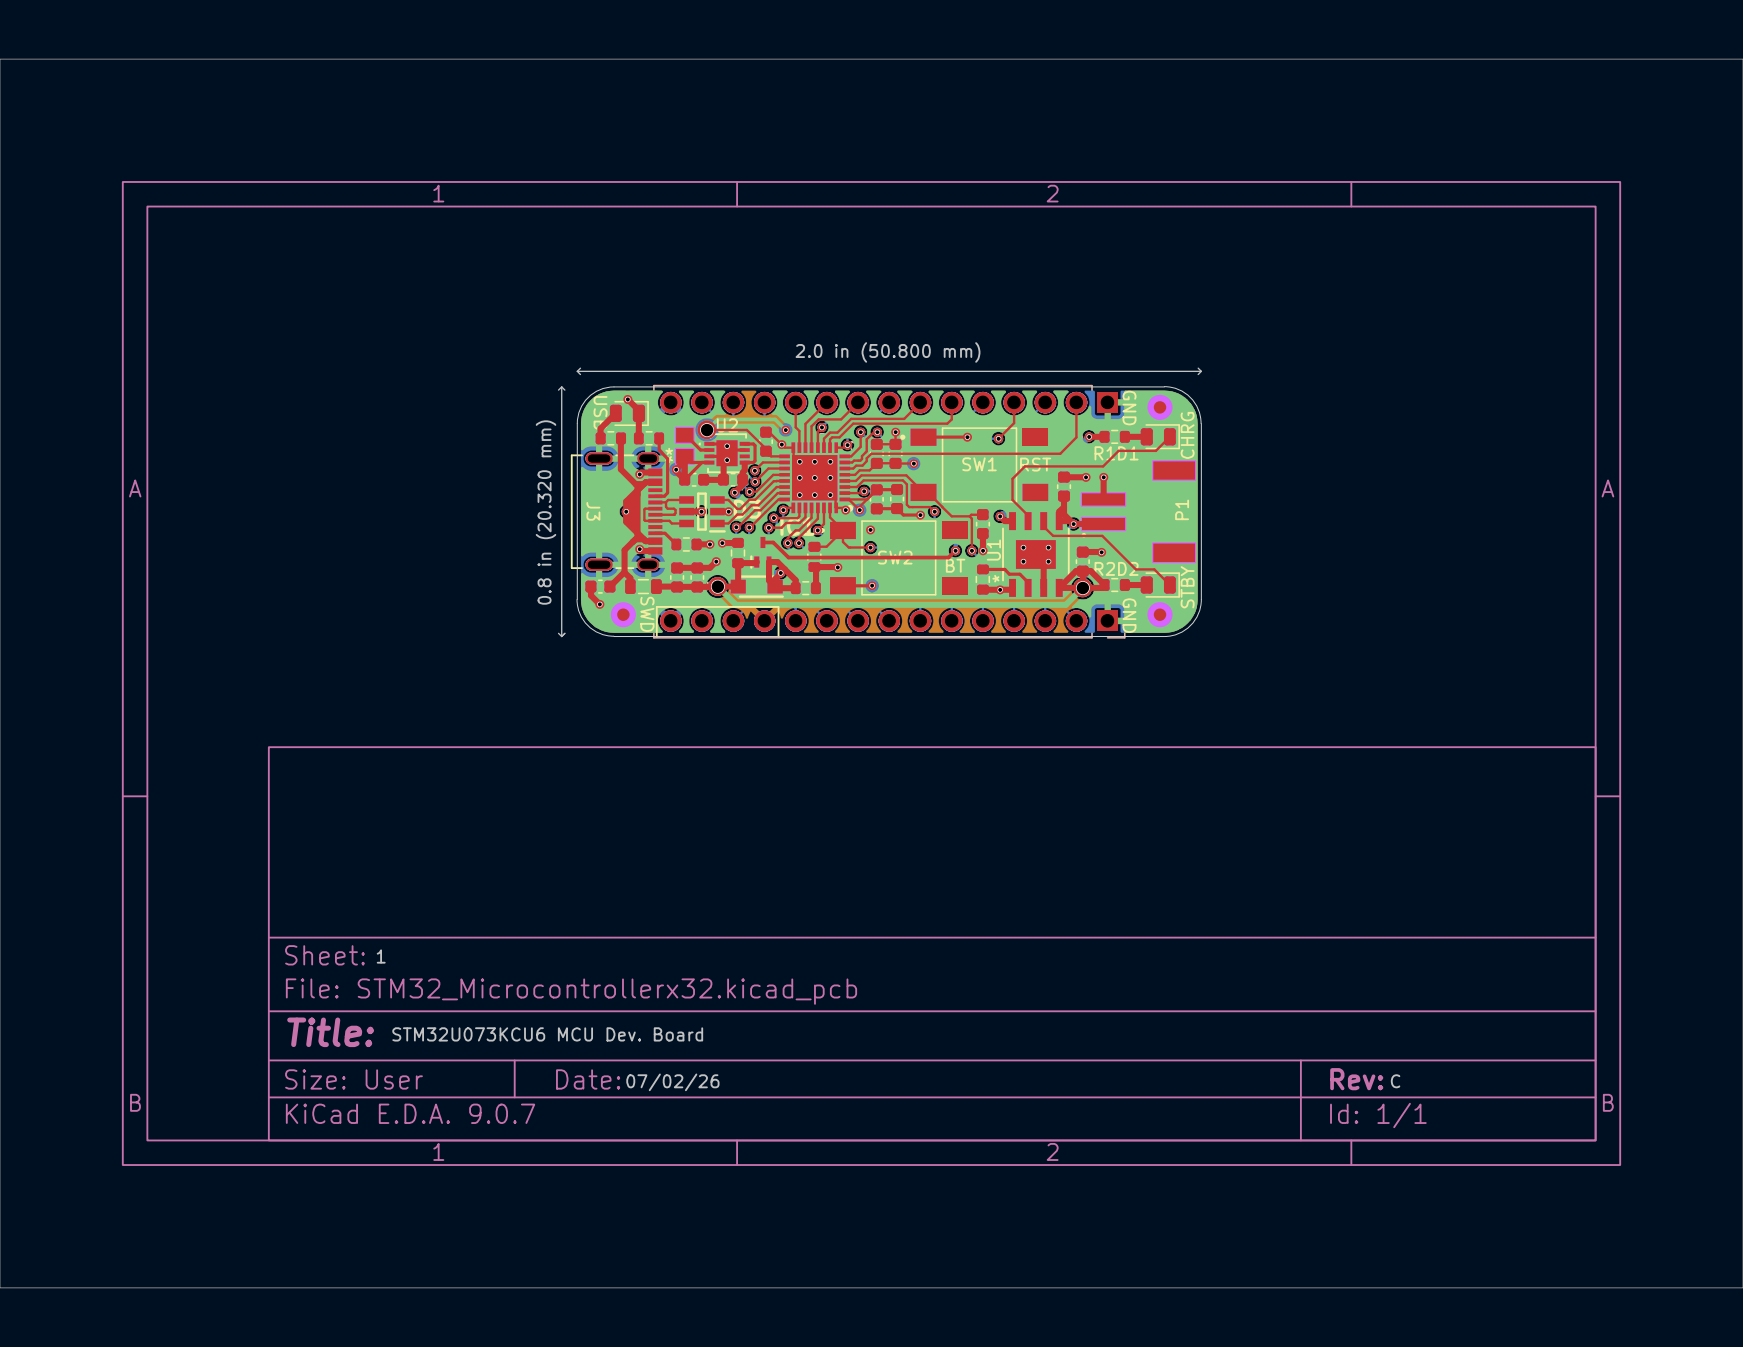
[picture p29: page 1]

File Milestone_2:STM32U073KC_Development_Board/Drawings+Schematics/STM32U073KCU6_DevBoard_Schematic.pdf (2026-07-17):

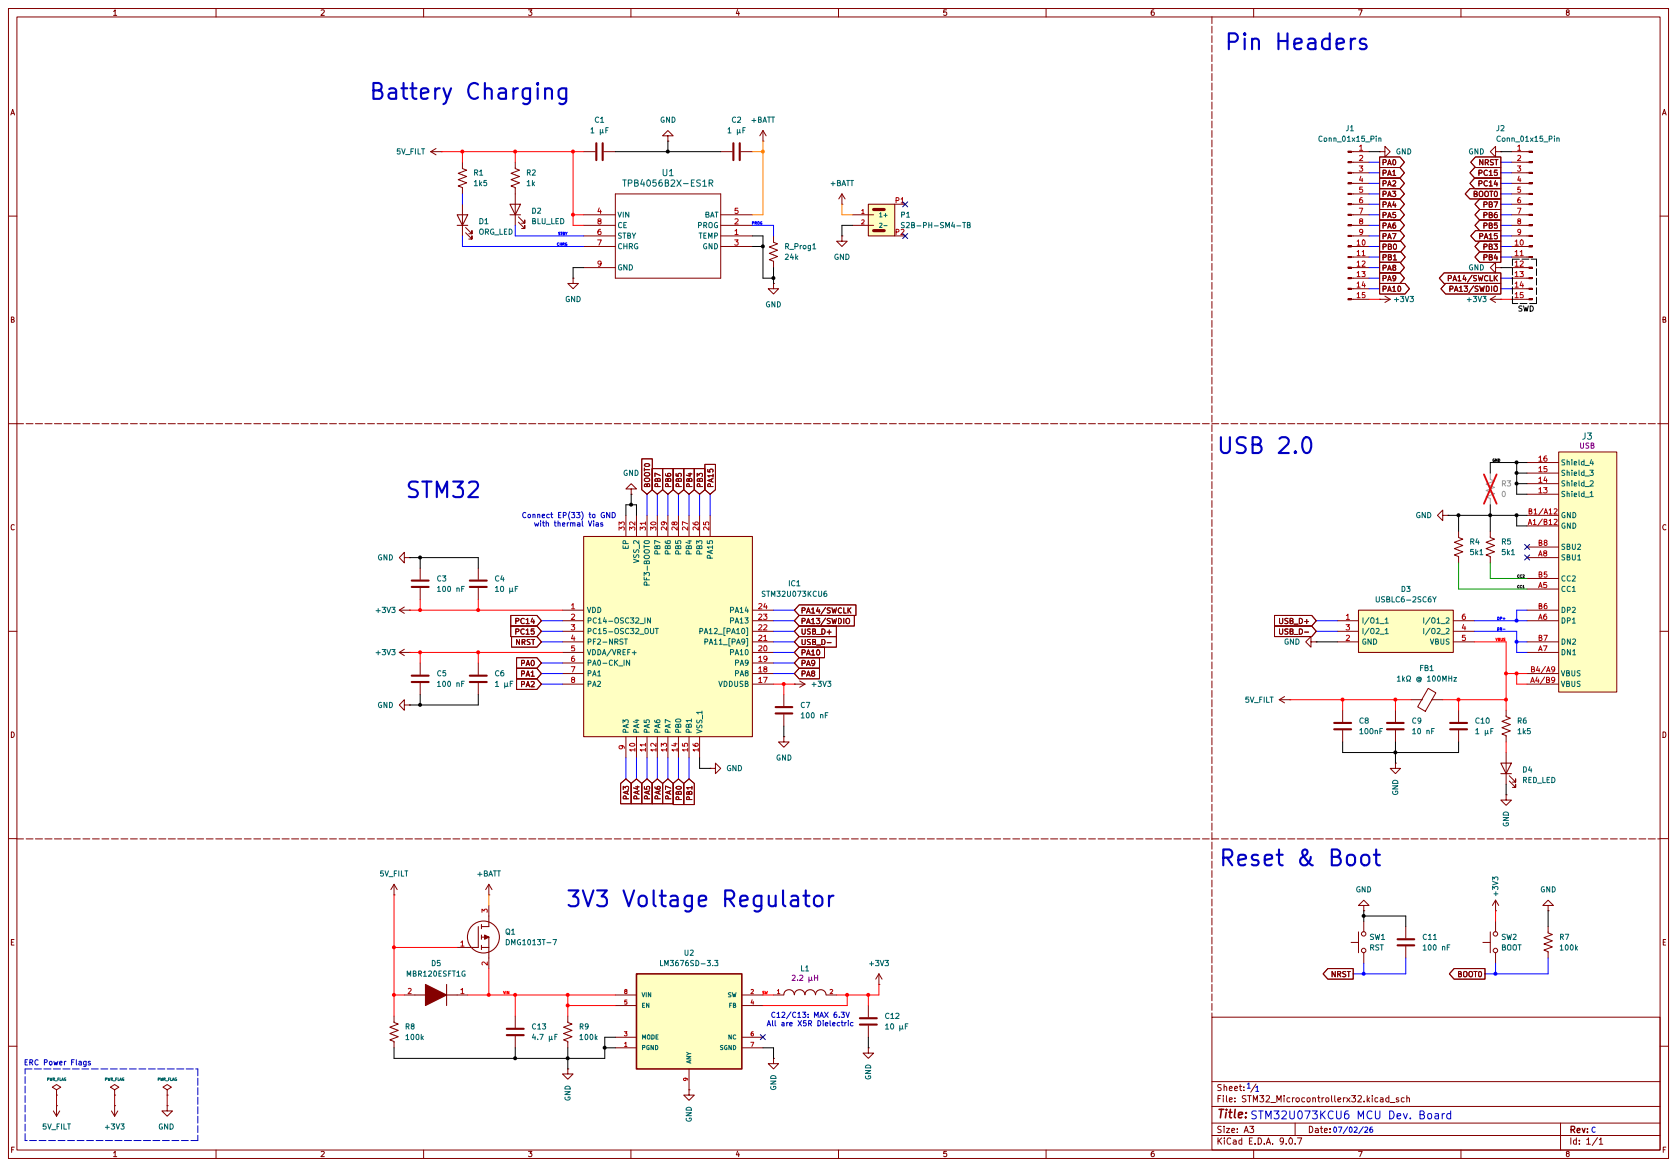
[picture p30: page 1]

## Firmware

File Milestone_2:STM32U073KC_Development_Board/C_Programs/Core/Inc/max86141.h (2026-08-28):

/**
 * @file max86141.h
 * @brief Header file for Max86141 HR/Sp02 sensor integration
 * @author Ryan Rau
 * @version 1.0
 * @date August 27th, 2026
 *
 * @see https://www.analog.com/media/en/technical-documentation/data-sheets/max86140-max86141.pdf
 */

/*
 * max86141.h
 *
 * Driver for the MAX86141 optical AFE, configured for GREEN-LED HEART
 * RATE ONLY with direct ambient sampling (Figure 2 in the datasheet).
 *
 * Board LED wiring: LED1 = Red, LED2 = IR, LED3 = Green.
 * Heart rate uses the green LED, so this driver drives LED3.
 *
 * Target: STM32U073KCU6, using the hardware SPI1 peripheral.
 *
 * Pin map (as configured in CubeMX):
 *   PA4 = CS   (plain GPIO output, NOT SPI1_NSS -- software-controlled
 *               so a single CS-low pulse can span a multi-byte burst
 *               FIFO read)
 *   PA6 = MISO (SPI1_MISO, AF)
 *   PA7 = MOSI (SPI1_MOSI, AF)
 *   PA1 = SCLK (SPI1_SCK, AF)
 *
 * SPI1 must be configured in CubeMX as: Full-Duplex Master, 8-bit data,
 * MSB first, CPOL = Low, CPHA = 1 Edge (SPI Mode 0), Hardware NSS
 * disabled, prescaler chosen to keep SCLK <= 4 MHz.
 */

#ifndef MAX86141_H
#define MAX86141_H

#include "stm32u0xx_hal.h"
#include <stdint.h>

// SPI configurations
#define MAX_CS_PORT     GPIOA
#define MAX_CS_PIN      GPIO_PIN_4
#define MAX_SPI_TIMEOUT_MS 100

/* Register addresses & Configuration bits */
#define MAX86141_WRITE 0x00
#define MAX86141_READ 0x80

#define MAX86141_REG_INT_STATUS1        0x00 // correct
#define MAX86141_REG_INT_STATUS2        0x01 // correct
#define MAX86141_REG_INT_ENABLE1        0x02 // correct
#define MAX86141_REG_INT_ENABLE2        0x03 // correct

#define MAX86141_REG_FIFO_WR_PTR        0x04 
#define MAX86141_REG_FIFO_RD_PTR        0x05 
#define MAX86141_REG_OVF_COUNTER        0x06
#define MAX86141_REG_FIFO_DATA_COUNT    0x07
#define MAX86141_REG_FIFO_DATA          0x08
#define MAX86141_REG_FIFO_CONFIG1       0x09
#define MAX86141_REG_FIFO_CONFIG2       0x0A 
    // FIFO_CONFIG2 bit positions
    #define MAX86141_FIFO_CFG2_FLUSH_FIFO    (1 << 4)
    #define MAX86141_FIFO_CFG2_FIFO_STAT_CLR (1 << 3)
    #define MAX86141_FIFO_CFG2_A_FULL_TYPE   (1 << 2)
    #define MAX86141_FIFO_CFG2_FIFO_RO       (1 << 1)

#define MAX86141_REG_SYSTEM_CTRL        0x0D 
    // System Control bit positions
    #define MAX86141_SYSCTRL_SINGLE_PPG     (1 << 3)
    #define MAX86141_SYSCTRL_LP_MODE        (1 << 2)
    #define MAX86141_SYSCTRL_SHDN           (1 << 1)
    #define MAX86141_SYSCTRL_RESET          (1 << 0)

#define MAX86141_REG_PPG_SYNC_CTRL      0x10 
#define MAX86141_REG_PPG_CONFIG1        0x11 
    // Register 0x11 layout: [ALC_DISABLE][ADD_OFFSET][PPG2_ADC_RGE 5:4][PPG1_ADC_RGE 3:2][PPG_TINT 1:0] (Pgs 55 & 68)
    // ADC current ranges (0x0 = ~4uA, 0x1 = ~8uA, 0x2 = ~16uA, 0x3 = ~32uA)
    // Pulse width/integration time (0x0 = 15.8us, 0x1 = 29.4us, 0x2 = 58.7us, 0x3 = 117.3us)
    #define ALC_DISABLE  0x0 // Enabled
    #define ADD_OFFSET   0x0 // No offset
    #define PPG2_ADC_RGE 0x2 // 16uA range
    #define PPG1_ADC_RGE 0x2 // 16uA range
    #define PPG_TINT     0x3 // 117.3us integration time
#define MAX86141_REG_PPG_CONFIG2        0x12 
    // Register 0x12 layout: [PPG_SR 7:3][SMP_AVE 3:0] (Pg 55)
    // Refer to Page 69 of datasheet for sample rates
    // Refer to Page 70 of datasheet for sample averaging
    // Note: True sample rate = PPG_SR/SMP_AVE (Ex: 128 sps (base)/2 avg = 64 sps)
    #define PPG_SR       0x0E // 128 sps
    #define SMP_AVE      0x01 // 2 averaged 
#define MAX86141_REG_PPG_CONFIG3        0x13 
    // Register 0x13 layout: [LED_SETLNG 7:6][DIG_FILT_SEL][-][-][BURST_RATE 2:1][BURST_EN] (Pg 55)
    // LED Settling (0x0 = 4us, 0x1 = 6us, 0x2 = 8us, 0x3 = 12us) (Pg 71)
    // Digital Filter Selection (0x0 = CDM, 0x1 = FDM) (Pg 72)
    // Burst Rate (0x0 = 8Hz, 0x1 = 32Hz, 0x2 = 84Hz, 0x3 = 256Hz) (Pg 72)
    // Burst En (0x0 = Disabled, 0x1 = Enabled) (Pg 72)
    #define LED_SETLNG   0x3 // 12 us
    #define DIG_FILT_SEL 0x1 // FDM
    #define BURST_RATE   0x0 // 8 Hz
    #define BURST_EN     0x0 // Disabled

#define MAX86141_REG_PROX_INT_THRESH    0x14 
#define MAX86141_REG_PHOTO_DIODE_BIAS   0x15 
    // Register 0x15 layout: [-][PDBIAS2 6:4][-][PDBIAS1 2:0] (Pg. 55)
    // Photodiode Bias capacitance (0x1 = 0-65pF, 0x5 = 65-130pF, 0x6 = 130-260pF, 0x7 = 260-520pF) (Pg 73)
    #define PDBIAS1 0x1 // 0-65pF
    #define PDBIAS2 0x1 // 0-65pF
#define MAX86141_REG_PICKET_FENCE       0x16 

// Registers used for sequencing LED flashes (Table 1 & 2 in datasheet, Pg 15) 
#define MAX86141_REG_LED_SEQ1           0x20 
#define MAX86141_REG_LED_SEQ2           0x21 
#define MAX86141_REG_LED_SEQ3           0x22 
    // LED Sequence register defenitions
    #define LEDC1 0x1 // Pulse LED1 (Red)
    #define LEDC2 0x2 // Pulse LED2 (IR)
    #define LEDC3 0x3 // Pulse LED3 (Green)
    #define LEDC4 0x0 // No pulse
    #define LEDC5 0x0 // No pulse
    #define LEDC6 0x0 // No pulse

#define MAX86141_REG_LED1_PA            0x23  /* Red */
#define MAX86141_REG_LED2_PA            0x24  /* IR */
#define MAX86141_REG_LED3_PA            0x25  /* Green */
    // LED CURRENTS (mA) (DO NOT EXCEED SELECTED RANGE)
    #define LED1_CURR 2.5f  // Red
    #define LED2_CURR 5.0f  // IR
    #define LED3_CURR 15.0f // Green
#define MAX86141_REG_LED_RANGE1         0x2A
    // Register 0x2A layout: [–][–][LED3_RGE 5:4][LED2_RGE 3:2][LED1_RGE 1:0]
    // LED current ranges (0x0 = 31mA, 0x1 = 62mA, 0x2 = 93 mA, 0x3 = 124 mA)
    #define LED1_RGE 0x0 // 31 mA
    #define LED2_RGE 0x0 // 31 mA
    #define LED3_RGE 0x1 // 62 mA

// Define the 8-bit register value for LED currents based on the chosen LED range
#define LED1_CURR_VAL (uint8_t) (LED1_CURR / (31 * ((int) LED1_RGE + 1)) * 256)
#define LED2_CURR_VAL (uint8_t) (LED2_CURR / (31 * ((int) LED2_RGE + 1)) * 256)
#define LED3_CURR_VAL (uint8_t) (LED3_CURR / (31 * ((int) LED3_RGE + 1)) * 256)

#define MAX86141_REG_PART_ID            0xFF

/* FIFO tag values we care about (Table 3 in datasheet, Page 16) */
#define MAX86141_TAG_PPG1_LEDC1   0x01  /* PPG1, Red LED exposure       */
#define MAX86141_TAG_PPG1_LEDC2   0x02  /* PPG1, IR LED exposure        */
#define MAX86141_TAG_PPG1_LEDC3   0x03  /* PPG1, Green LED exposure     */
// #define MAX86141_TAG_PPG1_LEDC4   0x04  /* PPG1, direct ambient sample  */
#define MAX86141_TAG_PPG2_LEDC1   0x07  /* PPG2, Red LED exposure       */
#define MAX86141_TAG_PPG2_LEDC2   0x08  /* PPG2, IR LED exposure        */
#define MAX86141_TAG_PPG2_LEDC3   0x09  /* PPG2, Green LED exposure     */
// #define MAX86141_TAG_PPG2_LEDC4   0x0A  /* PPG2, direct ambient sample  */
#define MAX86141_TAG_INVALID      0x1E  /* attempted read of empty FIFO */


// grab externally defined spi
extern SPI_HandleTypeDef hspi1;

/* One decoded FIFO sample */
typedef struct {
    uint8_t  tag;     /* 5-bit value, left-justified */
    uint32_t value;   /* 19-bit ADC value, right-justified */
} MAX86141_Sample;

typedef void (*MAX86141_SampleCallback)(const MAX86141_Sample *sample);

// Ensure MX_SPI1_Init() is called prior to MAX86141_INIT
void     MAX86141_Init(void);
void     MAX86141_Poll(MAX86141_SampleCallback cb);

void     MAX86141_WriteReg(uint8_t addr, uint8_t data);
uint8_t  MAX86141_ReadReg(uint8_t addr);
void     MAX86141_ReadFifoBurst(uint8_t *buf, uint16_t numBytes);

void     MAX86141_Shutdown(void);

#endif /* MAX86141_H */

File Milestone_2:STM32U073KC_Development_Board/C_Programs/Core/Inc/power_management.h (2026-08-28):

/**
 * @file power_management.h
 * @brief Header file for functions pertaining to device power usage
 * @author Ryan Rau
 * @version 1.0
 * @date August 27th, 2026
 */

#ifndef POWER_MANAGEMENT_H
#define POWER_MANAGEMENT_H

#include "stm32u0xx_hal.h"
#include <stdbool.h>

#define USB_DETECTION_PORT       GPIOB
#define USB_DETECTION_PIN        GPIO_PIN_3
#define PWR_BTN_GPIO_Port        GPIOA          
#define PWR_BTN_GPIO_Pin         GPIO_PIN_2 
#define PWR_WKP_PIN_POL PWR_WAKEUP_PIN4_LOW   
#define PWR_WKP_PIN_FLAG PWR_FLAG_WUF4

#define BTN_ACTIVE_LOW       1    // Button actives on low read
#define DEBOUNCE_MS          30
#define PWR_OFF_MS           800  // Time pressed before Power off

// Function definitions
bool USB_IsPluggedIn(void);
bool Pwr_Btn_IsPressed(void);
void Pwr_Btn_CheckForPress(void);
void EnterShutdown(void);

// external required functions
extern void MAX86141_Shutdown(void);
extern void ST7735_Shutdown(void);

#endif

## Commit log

2026-05-16 Added Datasheet for the microprocessor
    STM32UO73KC
2026-05-17 Added ZIF connector
2026-05-19 Checked off LEDs
2026-05-19 Added LED Datasheet
